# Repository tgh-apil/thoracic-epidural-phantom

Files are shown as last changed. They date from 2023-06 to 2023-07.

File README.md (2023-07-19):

# APIL Normal Thoracic Spine Epidural Phantom

thoracic spine both small

https://github.com/tgh-apil/thoracic-epidural-phantom/assets/84343976/2604490d-a012-4d1f-9888-fdd0e5aba910

3D Printed thoracic (T6 to T12) epidural spine based on CT data. The spine has been curved to allow for improved and more realistic access to the thecal sac, as demonstrated in the video above. Our epidural spine phantom is encased in an echogenic and shelf-stable synthetic gel which has a realistic tactile feel similar to human muscle. We can augment the echogenic properties to be transparent (clear gel) or to mimic that of biological tissue (opaque) based on the learning objective. Additionally, the Thoracic Spine Epidural Phantom contains an echogenic faux-thecal sac to replicate loss-of resistance on puncture. The faux-thecal sac can be inflated with water to simulate spinal fluid.

This model was developed at the [Lynn & Arnold Irwin Advanced Perioperative Imaging Lab](https://apil.ca/), Toronto General Hospital, University Health Network.

# Purchasing Information

To purchase this phantom, please email apil@uhn.ca and a representative will be in touch with you with more details.

A purchased phantom contains the following:
1. Fully assembled Normal Thoracic Spine Phantom
2. Custom table clamp to hold phantom to table surface

# Ultrasound Images

Coming soon

# Care and Maintenance

1. Apply generous amount of ultrasound gel to surface of phantom.
2. Inflate thecal sac with water and ensure quickturn locks are closed

# Materials & Equipment
## Hardware

* 6 x M4 6mm screws
* 4 x M4 8mm screws
* 11 x M4 12mm screws
* 4 x M4 14mm screws (for use with lid)
* 4 x M4 20mm (for use with case bottom)
* 2 x Quick-turn Lock
* 8 mm ID Silicone Tubing (as low durometer as possible)
* 2 x Tube Fittings

## Printing Equipment

* Polylactic Acid (PLA)
* Bridge Nylon
* Fused Deposition Modelling 3D printer

## Casting Equipment

* Ballistics Gel
  * 50/50 mixture by weight of [20% ballistics gel from Clear Ballistics](https://www.clearballistics.com/shop/20-ballistic-gelatin-nato-block-16x6x6/) and [Gelatin #5 from Humimic Medical](https://humimic.com/product/gelatin-5-medical-gel-by-the-pound/)
  * [Gel dye from Humimic Medical](https://humimic.com/product-category/dye/) (optional)
* Graphite Powder (optional)
  * Used to replicate echogenic scatter of muscle
* Slowcooker
* Silicone Mold Release Agent
* Two-part Platinum Cure Silicone Rubber (or equivalent)
  * Available from [Smooth-On](https://www.smooth-on.com/products/mold-star-trade-31t/)
* Degas Chamber (optional)
* Heat Gun (optional)

# Assembly Instructions

## Printing

This repo includes stl files for each printed part.

In general, we use the following settings for all parts of this phantom:

|Material      |	Colour  |	Nozzle Temp (C) |	Bed Temp (C) |	Infill (%) |	Perimeters (#) |
| ------------ | ------- | --------------- | ------------ | ---------- | -------------- |
| PLA          |	White   |	210.0           |	60.0         |	10.0       |	2              |
| Bridge Nylon |	Natural |	250.0           |	80.0         |	15.0       |	3              |

## Silicone Mold Casting

thoracic mold and insert
*Silicone mold (left), and insert with overhangs and tubing (right).*

1. Print all components in the directory */molds/* using the PLA printing settings outlined above.
2. Assemble outer mold parts 1 and 2 and together using:
   1. 6 x M4 6mm screws
3. Place inner mold parts 1 and 2 into the assembled outer parts and attach them using:
   1. 5 x M4 12mm screws (inner part 1)
   2. 6 x M4 12mm screws (inner part 2)
4. Spray the inside of the mold with a silicone mold release agent.
5. Mix 3700 g of silicone according to manufacturers instructions.
    - Degassing the silicone is optional but encouraged -- unless working with silicones with very short pot lives, such as Mold Star 31T.
    - Adding colourant to silicone is optional.
6. Pour all silicone into the assembled mold.
7. Allow silicone to cure according to manufacturer's instructions.
8. Carefully disassmble the mold and release the silicone.
    - NOTE: This step can be very difficult. Procede with caution and patience to avoid damaging the silicone shell.
9. Place the silicone mold into the two outer mold parts and screw the outer parts together with 4-6 M4 6mm screws. This will prevent the mold from deforming during the ballistics gel casting process.

## 3D-Printed Components

1. Print the thoracic spine (*/insert/thoracic spine insert.stl*) using the Bridge printing settings outlined above.
    - Ensure that there are **no/minimal supports in the spinal canal** where the thecal sac will pass through.
2. Print 2 insert overhangs (*/insert/insert overhang.stl*) using the PLA print settings outlined above.
3. Print all components in the directory */case/* using the PLA printing settings outlined above.
4. Carefully remove all supports from the parts when complete.

## Ballistics Gel Casting

1. **CAUTION:** Use appropriate heat-proof gloves when working with liquefied ballistic gel and/or heat gun.
2. **CAUTION:** work only in a very well ventilated area. A fumehood is highly recommended.

### Ballistics Gel Casting

#### Opaque Layer
If an opaque phantom is desired for use in ultrasound-guided epidural training, follow the steps below. If however the learning objective is to insert an epidural without the use of ultrasound, skip to the gel body section and use only clear gel.

1. Melt 97.5 g 20% gel, 97.5 g Humimic #5 gel, and 5 g of gel dye in crockpot @ 105C - 115C (approx. 225F - 240F), and stir once liquid to ensure an even distribution of dye. This is **200 g** of gel total, i.e. **2.5% dye** by weight, however the percentage of dye can be adjusted to achieve a desired opacity.
2. Pour into mold, then tilt the mold in a circular motion, ensuring the dyed gel coats the entirety of the bottom of the mold. Once the gel begins to cool and is moving very slowly, set aside and allow to cool completely.

#### Gel Body

1. Melt at least 850 g 20% gel and 850 g Humimic #5 gel (a total of **1700 g**) in crockpot @ 105C - 115C (approx. 225F - 240F).
2. Thread roughly 30 cm of silicone tubing through the spine insert to replicate the thecal sac.
3. Attach the two overhang parts to the spine insert using 4 x M4 8mm screws. 
4. Use a heat gun to gently melt the top of the dyed gel (if applicable).
5. Pour in gel until it reaches the top of the mold.
6. Place the insert spine side down into the mold, ensuring the overhang components bracket the sides of the mold. Weigh down the insert to prevent air bubbles.
7. Allow gel to fully cool before removing from silicone mold.

## Phantom Assembly

1. Insert spine with gel block into printed case.
2. Thread both ends of silicone tubing through printed case.
3. Attach case bottom with 4 x M4 20mm screws.
4. Attach case lid with 4 x M4 14mm screws.
5. Attach a tube fitting to each end of the silicone tube.
6. Attach a quick-turn lock to each end of the tube fittings.

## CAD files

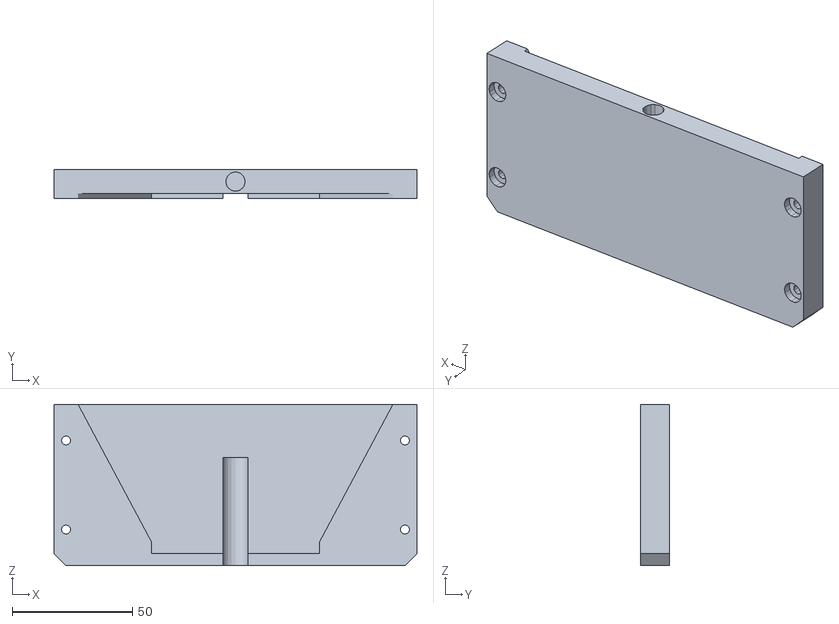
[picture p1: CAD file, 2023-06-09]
case/spine_epidural_phantom_case_bottom.stl
150.9 x 12.0 x 67.0

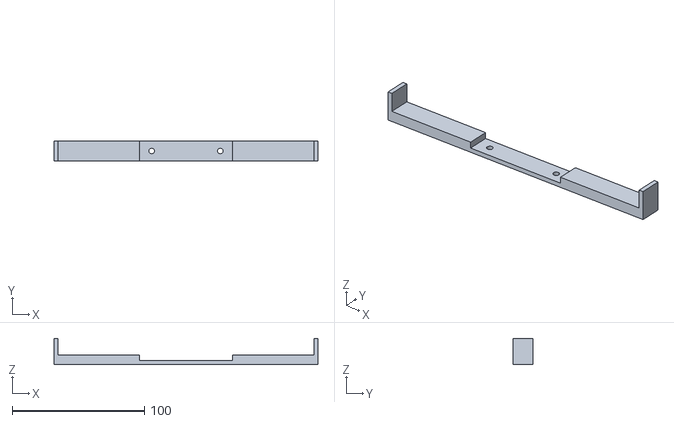
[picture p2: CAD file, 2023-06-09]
insert/insert overhang.stl
200.0 x 15.0 x 20.0

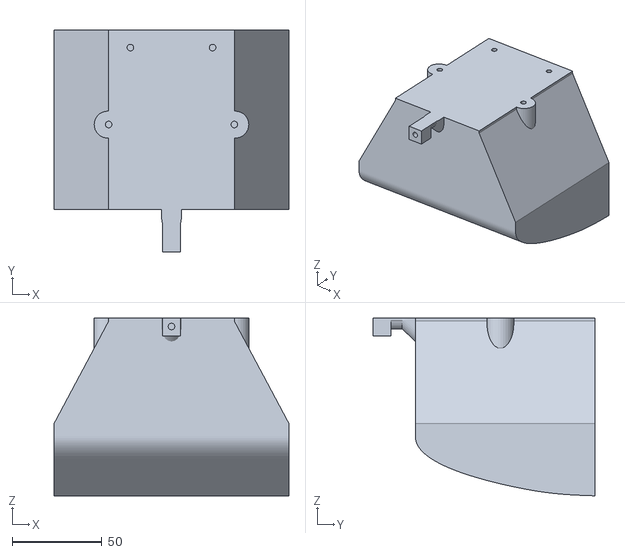
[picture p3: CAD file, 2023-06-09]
molds/thoracic mold inner 1.stl
130.9 x 123.5 x 98.9

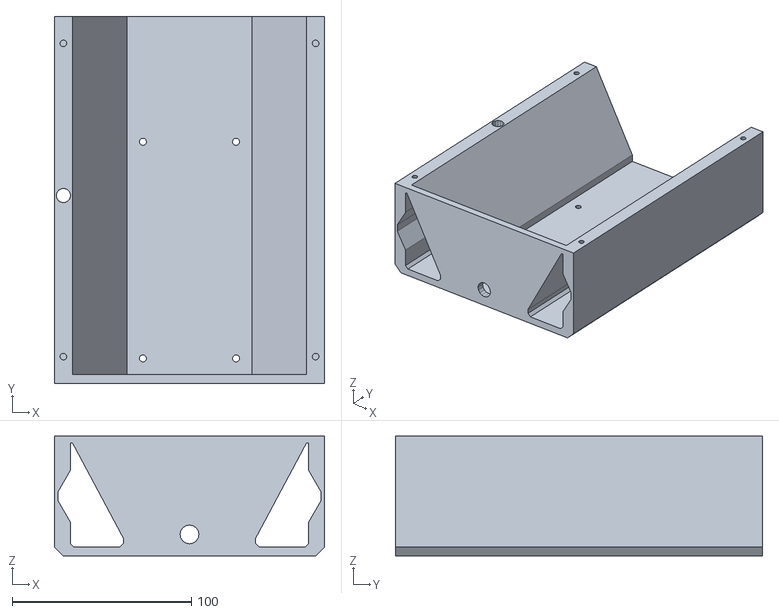
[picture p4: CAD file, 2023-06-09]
case/spine_epidural_phantom_case.stl
150.9 x 205.0 x 67.0

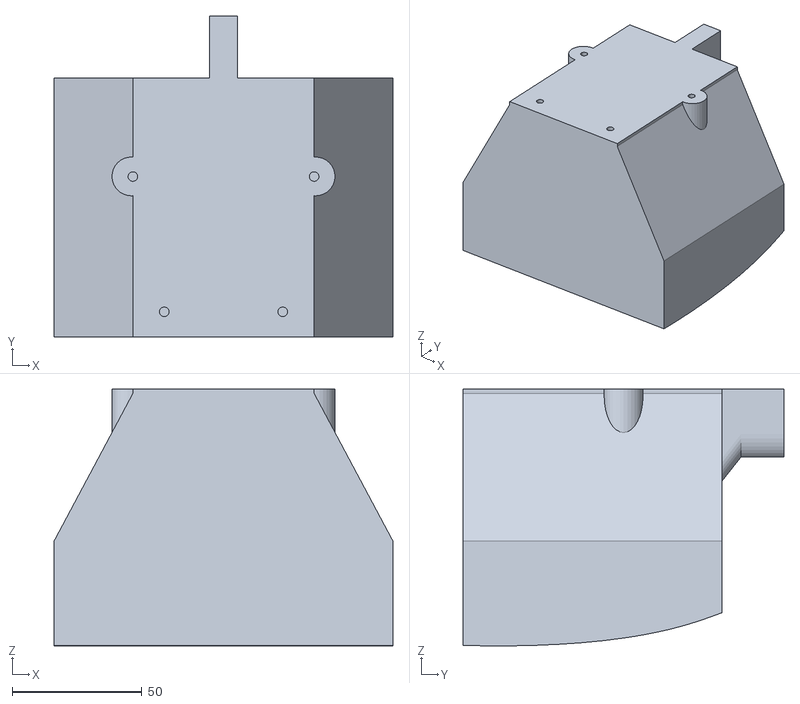
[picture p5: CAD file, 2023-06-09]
molds/thoracic mold inner 2.stl
130.9 x 123.9 x 99.1

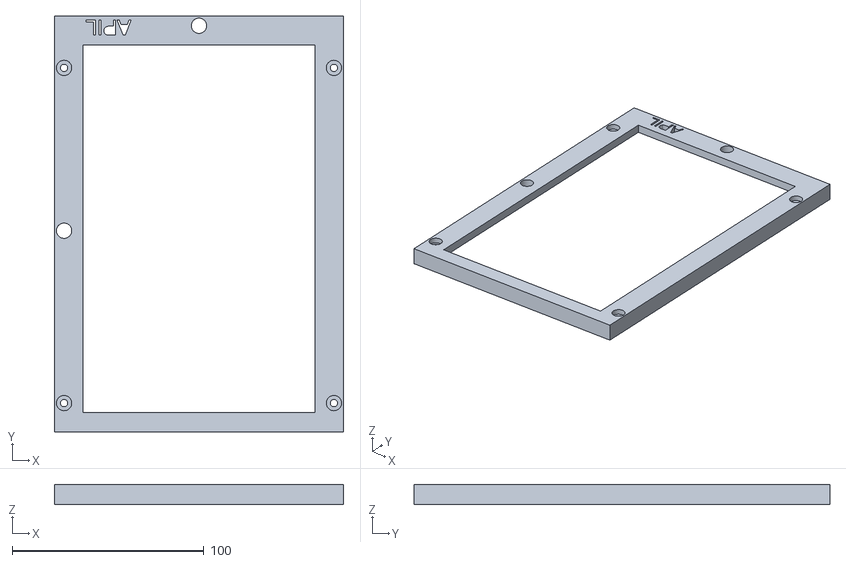
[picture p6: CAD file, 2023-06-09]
case/spine_epidural_phantom_lid_5mm.stl
150.9 x 217.0 x 10.5

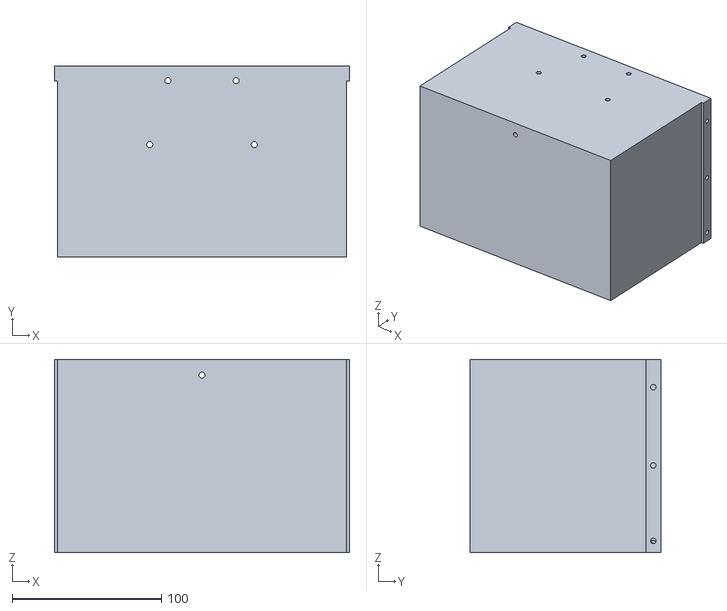
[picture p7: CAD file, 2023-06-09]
molds/thoracic mold outer 1.stl
197.5 x 127.8 x 129.4

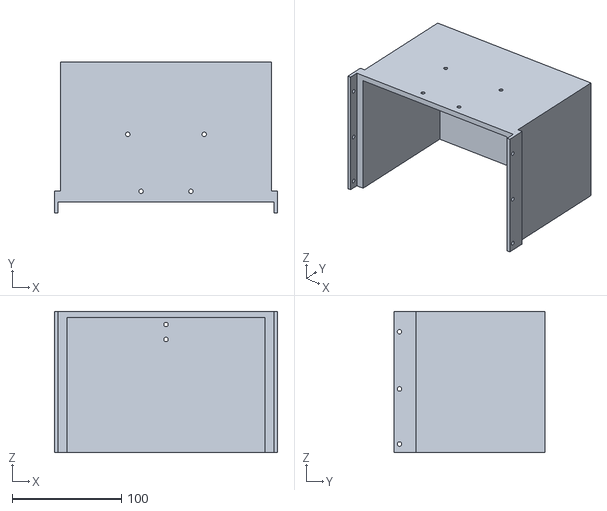
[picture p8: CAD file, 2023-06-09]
molds/thoracic mold outer 2.stl
204.3 x 138.1 x 129.4

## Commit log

2023-06-09 adding insert stl file
2023-06-09 adding intermediate mold stl files
    [thoracic mold inner 1.stl, thoracic mold inner 2.stl, thoracic mold outer 1.stl, thoracic mold outer 2.stl]
